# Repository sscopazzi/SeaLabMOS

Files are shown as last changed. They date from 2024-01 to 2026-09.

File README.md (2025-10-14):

This work will be presented at MTS Great Lakes in 2025. If curious, I can send you the paper in prep, or check out [my website's page](https://www.sophiescopazzi.com/projects/sealabmos) for some pictures.

## Current Supported System Types

1. **Traditional CTD**: Salinity, temperature, depth sensors with three variants: 1.5in and 2.0in PVC (~140m) or 2.0in steel pipe (~350m)  
2. **Temperature logger**: Temperature only monitoring for a ~few days to ~two weeks, based on system configuration
3. **Bottom Pressure Recorder**: Pressure only for tide measuring, research ongoing for three used in conjuction for wave height and direction
4. **Surface Float**: All sensors optional. Salinity, water temperature, GNSS/location, LED beacon, atmospheric pressure/temperature, light, etc.



### Base Datalogger Hardware

| **Name** | **Adafruit Part** # | **What it does** | **Accuracy** | **Cost** |
|------|------------------|---------------|----------|------|
| [Adafruit Feather RP2040 Adalogger w/ microSD Card](https://www.adafruit.com/product/5980) | 5980 | Datalogger | — | \$15 |
| [SD/MicroSD Memory Card (512 MB)](https://www.adafruit.com/product/5252) | 5252 | Data storage | — | \$5 |
| [DS3231 Precision RTC FeatherWing](https://www.adafruit.com/product/3028) | 3028 | Real time clock | ±2 minutes per year | \$14 |
| [CR1220 12mm Diameter 3 V Lithium Coin Cell Battery](https://www.adafruit.com/product/380) | 380 | Battery for RTC | — | \$1 |
| [Lithium Ion Battery Pack 3.7 V 2.2 Ah (or 2.5–10 Ah)](https://www.adafruit.com/product/1781) | 1781 (2.2 Ah) | Battery | — | \$10 |
|      |      |      |      |      |
|      |      |      |      |      |
| **Display**     |      |      |      |      |
| [Adafruit FeatherWing 128×64 OLED Display (optional)](https://www.adafruit.com/product/4650) | 4650 | Screen, buttons | — | \$15 |
|      |      |      |      |      |
|      |      |      |      |      |
| **Location**      |      |      |      |      |
| [Mini GPS (PA1010D)](https://www.adafruit.com/product/4415) | 4415 | GPS/GNSS, Time | Testing 10 Hz | \$30 |
| [Ultimate GPS Breakout (PA1616D)](https://www.adafruit.com/product/5440) | 5440 | GPS/GNSS, Time | Testing, 10 Hz | \$30 |
| [External Active GPS Antenna](https://www.adafruit.com/product/960) | 960 | For Ultimate | Testing | \$21.5 |
| [High-strength 'rare earth' magnet](https://www.adafruit.com/product/9) | 9 | Hold antenna | — | \$2.5 |
|      |      |      |      |      |
|      |      |      |      |      |
| **Sensor Cables**      |      |      |      |      |
| [STEMMA QT / Qwiic JST SH 4-pin Cable](https://www.adafruit.com/product/5385) | 5385 | Sensor connection | — | \$1–1.5 |
| [STEMMA QT / Qwiic 5 Port Hub](https://www.adafruit.com/product/5625) | 5625 | Sensor connection | — | \$2.5 |

### Sensors  

| **Type** | Part # | Variable | Depth Rating (m) | Response Time | Accuracy | Cost |
|---|---|---|---|---|---|---|
| [Atlas Scientific Mini Conductivity K 1.0 Kit](https://atlas-scientific.com/kits/mini-conductivity-k-1-0-kit/) | — | Conductivity | 353 | 90% in 1 s | 99% in 1 s | \$200 |
| [Waterproof 1-Wire DS18B20](https://www.adafruit.com/product/381) | 381 | Temperature | Not specified | 60% in 12 s, 90% in 31 s | ±0.5 °C | \$15 |
| [DS18B20 Extender](https://www.adafruit.com/product/5971) | 5971 | DS18B20 accessory board | — | — | — | \$— |
| [10K Precision Epoxy Thermistor](https://www.adafruit.com/product/372) | 372 | Temperature | Not specified | 60% in 3 s, 90% in 7 s | ±0.1 – 0.5 °C | \$4 |
| [Platinum RTD Sensor – PT100](https://www.adafruit.com/product/3290) | 3290 | Temperature | Not specified | — | — | \$— |
| [PT100 RTD Amplifier – MAX31865](https://www.adafruit.com/product/3328) | 3328 | Amplifier for PT100 | — | — | — | \$— |
| [Atlas Scientific K 1.0 Kit](https://atlas-scientific.com/kits/mini-conductivity-k-1-0-kit/) | — | Conductivity | 353 | 90% in 1 s | 90% in 1 s | \$200 |
| [Blue Robotics Celsius Fast-Response (TSYS01)](https://bluerobotics.com/store/sensors-cameras/sensors/celsius-sensor-r1/) | — | Temperature | 975 | 3 s (90% in 2 s, measured) | ±0.1 °C | \$70 |
| [Blue Robotics Bar02 / Bar30 / Bar100 (pressure options)](https://bluerobotics.com/product-category/sensors-cameras/sensors/) | — | Pressure | 10m, 300, 1,000m | — | — | \$80, \$90, \$380 |

> *Note:* Response time and accuracy are from manufacturer specs and initial testing. For reduced costs, static deployments may not need a pressure sensor.  
> Depth rating for temperature sensors not from Blue Robotics are not specified by manufacturers and depends on sealant/epoxy.

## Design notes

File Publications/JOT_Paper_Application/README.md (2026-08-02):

# Figures for "Conductivity Accuracy of Two Open Source SeaLabMOS CTDs"

Open `SeaLabMOS-JOT-app-paper.ipynb` and run all cells in order: the master CONFIG cell, the three loader sections, then any figure cell in any order. Figure cells never depend on each other. All paths are relative to the notebook, so this folder can be moved, zipped or cloned anywhere and still run.

To see photos of what the systems look like, [please see my website](https://www.sophiescopazzi.com/projects/sealabmos).

Figures are written to `plots/` as `figNN_*.png` at 600 dpi, numbered to match the paper. The list of required packages is fairly standard (there is an environment.yml if you need it).
  - python=3.12
  - numpy=2.4.4
  - pandas=3.0.2
  - scipy=1.17.1
  - matplotlib=3.10.8
  - xarray=2026.7.0
  - netcdf4=1.7.4 # conda package name is lowercase; imported as netCDF4
  - gsw=3.6.23 # TEOS-10 / PSS-78, provides gsw.SP_from_C

## Layout

Every data file sits directly in `data/`, prefixed by experiment. The two units MIS_1 and MIS_2 did not do the same things: MIS_1 was used on the workbench in the lab and MIS_2 was used for the stepped casts. Both took part in the bucket tests. In all cases, the ground truth was the RBR system.

```
SeaLabMOS-JOT-app-paper/
├── SeaLabMOS-JOT-app-paper.ipynb
├── README.md
├── environment.yml
├── requirements.txt
├── .gitignore
├── data/
│   ├── lab_MIS_1.csv                          lab standards, MIS_1
│   ├── lab_204386_20260703_1802.nc            lab standards, RBR          (+ .rsk)
│   ├── bucketA_MIS_1.csv                      Jul-3 bucket A, MIS_1
│   ├── bucketB_MIS_1.csv                      Jul-3 bucket B, MIS_1
│   ├── bucketA_MIS_2.csv                      Jul-3 bucket A, MIS_2
│   ├── bucketB_MIS_2.csv                      Jul-3 bucket B, MIS_2
│   ├── bucket_204386_20260703_1829.nc         Jul-3 buckets A and B, RBR  (+ .rsk)
│   ├── cast_MIS_2_2026-07-11T21-12-38.csv     Jul-11 stepped casts, MIS_2
│   ├── cast_204386_20260711_1639.nc           Jul-11 stepped casts, RBR   (+ .rsk)
│   └── static_frame/                          bottom-frame deployment, Jun 5-9
│       ├── long_originalCTD_2026-06-07T06-41-00.csv   co-deployment, originalCTD
│       ├── long_204386_20260609_2023_00008.nc         co-deployment, RBR
│       ├── profiles_originalCTD/              16 originalCTD casts
│       │   └── originalCTD_<stamp>.csv
│       └── profiles_rbr/                      17 RBR cast profiles
│           └── rbr_204386_<log>_<nnnnn>.nc
└── plots/                                     figNN_*.png at 600 dpi, tracked in git
```

## Figures

| Fig | Content |
|----|----|
| 1  | Experiment timeline |
| 2  | Lab setup photograph (not a plot, no cell in the notebook) |
| 3  | Temperature 1:1 vs RBR: pooled casts + static co-location |
| 4  | Implied EC gain, both units + MIS_1 pipeline |
| 5  | Depth vs time, both stepped casts |
| 6  | Firmware-reported salinity profiles |
| 7  | 1:1, firmware vs recalculated salinity at hold averages |
| 8  | EC_GAIN fit + two bucket-test insets |
| 9  | Four salinity pipelines vs RBR, MIS_1 workbench |
| 10 | Out-of-sample bucket validation for MIS_1 and MIS_2 |
| 11 | Salinity profiles: RBR, firmware and recalculated |
| 12 | GOFS 3.1 vertical level distribution |

## Corrections to Salinity Data

To sum up results of the paper in one sentence, MIS_1 and MIS_2 need a system-specific correction, applied to electrical conductivity before the PSS-78 call (never as an additive offset on salinity):

- **MIS_1**: quadratic, `EC_corr = 0.86331·C + 0.0149285·C²`, fit on the six lab
  calibration standards through the origin.
- **MIS_2**: scalar, `EC_corr = EC_GAIN_MIS2 · C`. MIS_2 never ran against the
  lab standards, so its gain comes from the thirteen equilibrated hold points of
  the 2026-07-11 stepped casts. It's `EC_GAIN_MIS2` = 0.9908. 

`C` used in is `gsw.SP_from_C` in mS/cm. The [Atlas Scientific salinity sensor (EZO)](https://atlas-scientific.com/kits/mini-conductivity-k-1-0-kit/) logs µS/cm, so every pipeline divides by 1000 beforehand. There is no single `EC_GAIN`. **Each correction is system-specific.**

`EC_GAIN_MIS2` is **fitted at run time**, not assumed. The hold points it is fit on carry whatever depths `DEPTH_ZERO_MODE` produces, so the gain and the depth
zero stay consistent. 

Firmware-reported salinity (`sal_fw`) is not corrected and **is not a data product**. It appears in Figures 6, 7 and 11 only to show why it is discarded. The EZO hard-codes 25 °C in its temperature compensation and applies no pressure term (that I can find information about).

## Data Notes

Every file is read by at least one figure, except the `.rsk` files, which are the RBR system originals kept for provenance. The notebook reads the `.nc` exports Ruskin produced from them.

| File | Used by |
|----|----|
| `lab_MIS_1.csv` | Figures 4, 9, 10 |
| `lab_204386_20260703_1802.nc` | Figures 4, 9, 10 |
| `bucketA_MIS_1.csv` | Figure 10 |
| `bucketB_MIS_1.csv` | Figure 10 |
| `bucketA_MIS_2.csv` | Figures 4, 8 inset, 10 |
| `bucketB_MIS_2.csv` | Figures 4, 8 inset, 10 |
| `bucket_204386_20260703_1829.nc` | Figures 8, 10 |
| `cast_204386_20260711_1639.nc` | Figures 5–8, 11 |
| `cast_MIS_2_2026-07-11T21-12-38.csv` | Figures 5–8, 11 |

Figures 1 and 12 require no data files. Figure 1 is built from hand-written timestamps in the loader CONFIG, Figure 12 from the transcribed GOFS [vertical level list](https://www.hycom.org/dataserver/gofs-3pt1/analysis).

The bottom of every RBR cast is trimmed by 0.1m where it contacted the muddy bottom, effecting the salinity value by sometimes up to 6.7 PSU (`RBR_BOTTOM_TRIM_M = 0.10`).

Figure 3 reads everything under `data/static_frame/`: the 17 `originalCTD_*.csv` casts, the 17 RBR cast profiles they pair against, and the long log. 16 are casts and 15 of those pair one-to-one with a profile; `originalCTD_2026-06-07T06-05-42.csv` has two casts in the same data file and thus is split into `_a` and `_b`. `long_originalCTD_2026-06-07T06-41-00.csv` is the long co-deployment and the loader selects it as `LONG`.

A keen viewer will see the numbers of the RBR casts are not sequential. Left out of `static_frame/profiles_rbr`: two RBR profiles `20260609_2023` numbers `_00002` and `_00020`, plus `20260606_0625_00001` where they do not have a paired cast.

Also missing are the two casts from the long deployment: `RBR_00007` is the descent into it and `RBR_00009` is the recovery. 

Nothing in the matcher looks at depth, so `MAX_DEPTH_MISMATCH_M = 1.0` in the pairing cell checks afterwards: a paired cast and profile should reach nearly
the same depth, and anything further apart is reported by name. It warns rather than drops, since a wide pair may still be legitimate. On the shipped data every pair passes, the worst being 0.38 m.

**For the stepped cast hold depth matching:** 15 holds are detected, but they become the 13 points in the Figure 8 because the RBR binned profile spans 0.22–9.80 m, and two MIS_2 surface holds sit above the RBRs shallowest bin with nothing to match against. Both are hold segments inside `cast_MIS_2_2026-07-11T21-12-38.csv` and are not separate files (two holds very 
close to the surface done with the MIS_2 and not RBR). These holds outside the binned RBR profile are dropped explicitly instead of silently taking an end-bin value.

## Font sizes

`FS_GLOBAL` in the master CONFIG controls every figure for consistency. 
Each figure cell opens with `fonts()`, which resets the six `FS_*` globals 
before drawing, so a size set inside one cell cannot leak into the next regardless 
of order ran. To change one figure only, pass the override to its own call, e.g. `fonts(FS_TICK=14)`, or just hardcode the line (as done in a few places for figure legibility and formatting).

## The SeaLabMOS Clocks and Time Issues

The absolute time from MIS_1 and MIS_2's clocks for the buckets was incorrect. On power-on the system initialised its clock to the firmware compile time, so the time record starts at the time that firmware was uploaded, regardless of true power-on time. This firmware bug has since been fixed. Elapsed time *within* one record is reliable and used for hold detection, transit rates, the Figure 5 time axis. 

The originalCTD and MIS_2's stepped cast (I found the firmware bug between the buckets and stepped cast) didn't have the time bug, but they carried a daylight-saving hour added to a UTC clock because the firmware was uploaded before DST happened (in the case of the originalCTD) or I put the wrong ZD in the firmware for DST (in the case of MIS_2).

- **Buckets are matched by which water.** Each instrument has its own window in its
  own clock. What ties them together is that both sampled the same bucket. The system's mean over its window is the reference salinity for the system in their respective buckets.
- **Casts are matched by time.** The Jul-11 stepped casts and the originalCTD casts carry a daylight-saving hour on an otherwise sound UTC clock; removing it (`MIS2_CAST_DST_FIX_H`, `APPLY_DST_FIX`) makes their timestamps directly comparable with the RBR, and cast-level pairing in the static-frame section is done on overlapping time interval, with maximum-depth agreement as an independent check.

## Atmospheric pressure and depth

Atmospheric pressure is **not** taken per cast from a barometer. `ATM_MBAR = 1013.25` is a nominal standard atmosphere, and the RBR independently uses its own default_atmospheric_pressure` of 10.1325 dbar, the same nominal value.

That constant enters results by two different routes.

**Through the PSS-78 pressure term.** `p_dbar` is passed to `gsw.SP_from_C`, where pressure barely matters: an error of 0.2 dbar moves salinity by 0.00005 PSU, and 2 dbar by 0.0005 PSU. This is why the bucket and lab work is unaffected regardless of the weather.

**Through the depth matching.** Each hold takes its reference by interpolating the RBR profile in depth, so a depth error maps straight onto a salinity error through the stratification.

### Zeroing the depth against in-air samples

`DEPTH_ZERO_MODE` in the master CONFIG selects what defines 0 m for MIS_2's stepped casts, using the samples where `ec` falls below `AIR_EC_MAX` (probe out of water). It changes Figures 5, 6, 7, 8 and 11; Figures 1, 4, 9, 10 and 12 are untouched.

| Mode | Offset subtracted | Fitted gain | Fit RMSE |
|----|----|----|----|
| `none` — firmware `brDepth` as-is | 0.0000 m | 0.9908 | 0.0629 PSU |
| `pre_cast_air` | 0.1488 m | 0.9898 | 0.0533 PSU |
| `post_cast_air` (default) | 0.0059 m | 0.9908 | 0.0626 PSU |

`post_cast_air` is the default: its in-air window sits after the cast, so it zeros the depth using the closest thermal state of the pressure sensor to the temperature of the water. 
 `none` gives the same 0.9908 the paper prints, because the firmware's own zero happens to land 0.0059 m from the post-cast in-air reading. This is luck rather than a reason to trust the firmware zero.

**The two in-air references disagree, and the reason is temperature, not weather.** The pressure reading moves with sensor temperature (roughly +2.9 mbar/°C within this record):

| In-air window | Sensor T | brPressure | brDepth |
|----|----|----|----|
| before the first cast (dry and hot from being in the sun, just powered on) | 26.1 °C | 1028.06 mbar | +0.1488 m |
| after the last cast (wet, 13 min later) | 21.1 °C | 1013.65 mbar | +0.0059 m |

Atmospheric pressure does not fall 14.5 mbar in 13 minutes. The sensor cooled 5 °C and the reading followed. During the casts the sensor sits at 20.3 °C (close to the post-cast in-air state), roughly 6 °C from the pre-cast one. So `pre_cast_air` derives its zero from both a thermal state the instrument was not in while measuring,  and from temperature warmer than the water, and `post_cast_air` derives it from very nearly the right one.

The loader prints all three offsets and the sensor temperature in each state on every run, and warns when the two in-air references differ by more than 0.05 m.

**Pre vs post-cast pressure is on our list for further study**. This should especially be compared to a weather station [like this one](https://github.com/sscopazzi/Portable_Weather_Station).

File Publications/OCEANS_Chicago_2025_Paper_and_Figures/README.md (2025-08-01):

# SeaLabCTD MTS Paper Deployments and Figures

This folder contains plots, results, and analysis scripts from the series SeaLabCTD tests conducted April to July 2025 conducted immitely offshore the Valdez Marine Termina, in Port Valdez, Prince William Sound, Alaska. Each folder represents a different deployment.

---

### Tools Used
- Python (pandas, matplotlib, numpy, scipy, etc.)
- GSW (Gibbs SeaWater) Oceanographic Toolbox
- Arduino + Feather RP2040 Logger Firmware (see manual)
- Atlas Scientific + Blue Robotics sensors
---

### Notes
- All data is timestamped ISO 8601 format with "-" substituted for ":" for filename restrictions.
- `.csv` files in each directory contain "cleaned" data (only the relevent downcast). Sometimes there are two downcasts.
- The figures below are in the MTS paper.
---

### Contact

For questions, please ask Sophie Scopazzi. Contact information on [my website](https://www.sophiescopazzi.com/)

---

### Figures Overview

All figures used in MTS paper. All figures are located in their respective test folders. Alt text is provided for accessibility.

### Figures Overview

All figures used in the MTS paper. All figures are located in their respective test folders. Alt text is provided for accessibility.

### Figures Overview

All figures used in the MTS paper. All figures are located in their respective test folders. Alt text is provided for accessibility.

| Figure | Description |
|--------|-------------|
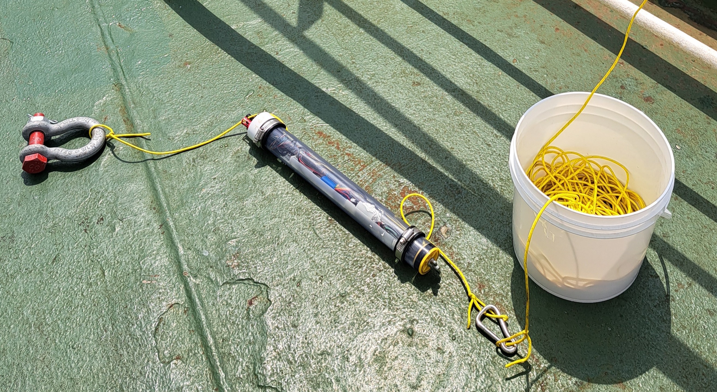
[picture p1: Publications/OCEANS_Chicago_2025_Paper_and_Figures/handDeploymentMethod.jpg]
Hand deployment with SeaLabCTD, shackle and bucket for rope
| **Hand Deployment**<br> | Method used to lower the CTD. A shackle is used as weight; a bucket prevents line tangling. |
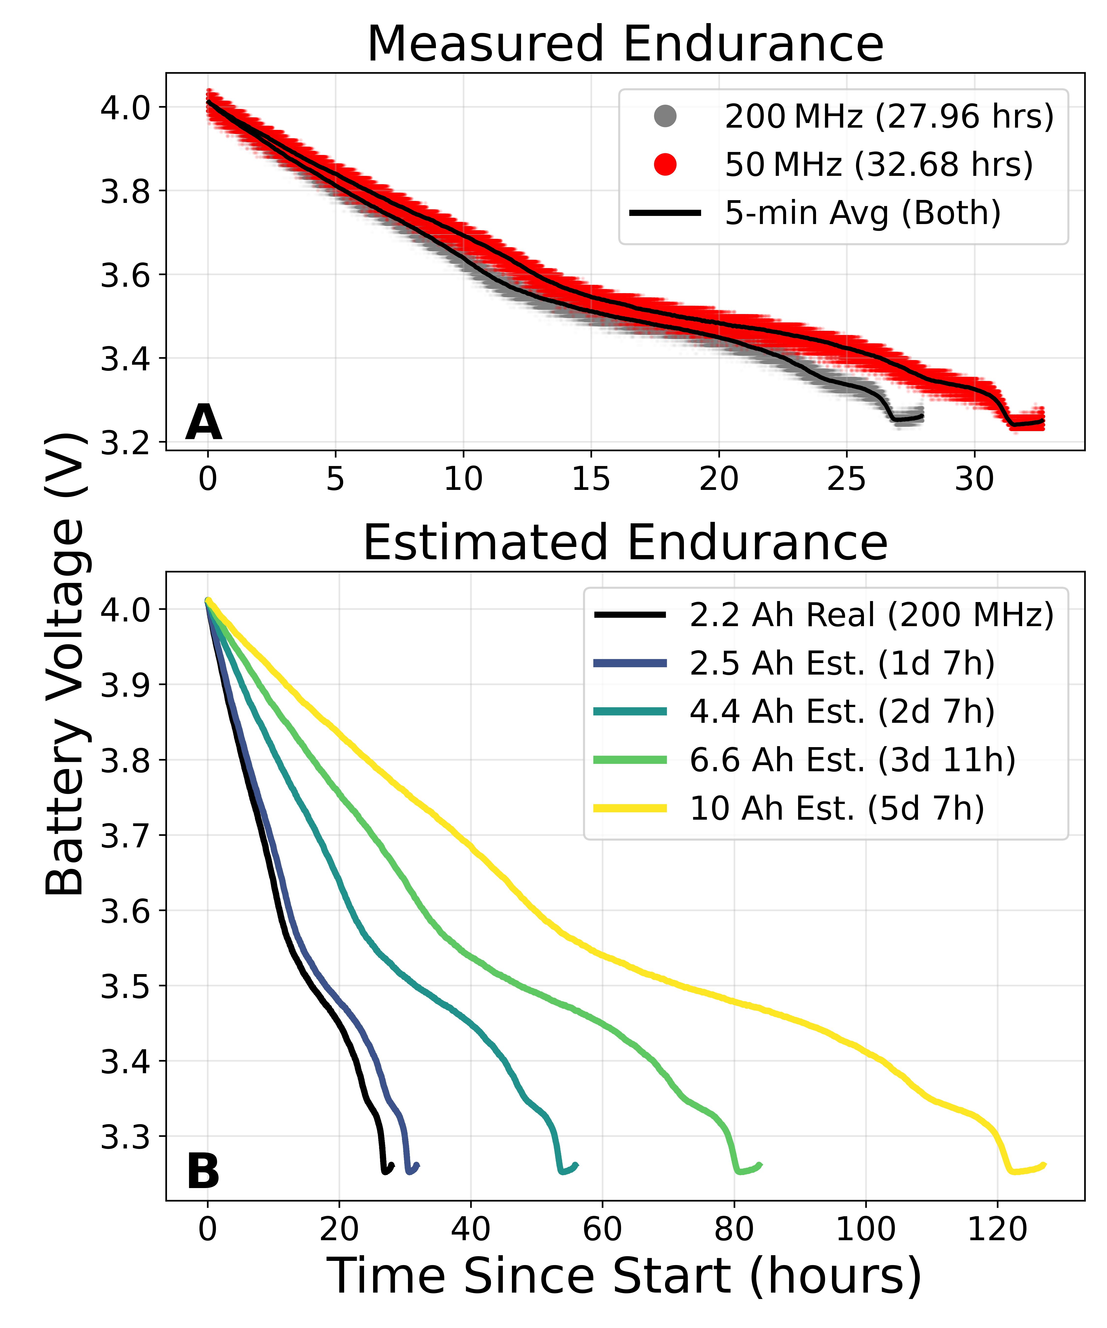
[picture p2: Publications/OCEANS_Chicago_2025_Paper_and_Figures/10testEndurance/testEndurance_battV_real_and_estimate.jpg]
Battery test results showing endurance vs clock speed
| **Battery Endurance**<br> | Runtime comparison at 200 MHz vs 50 MHz. Estimation of endurance for different Adafruit batteries. |
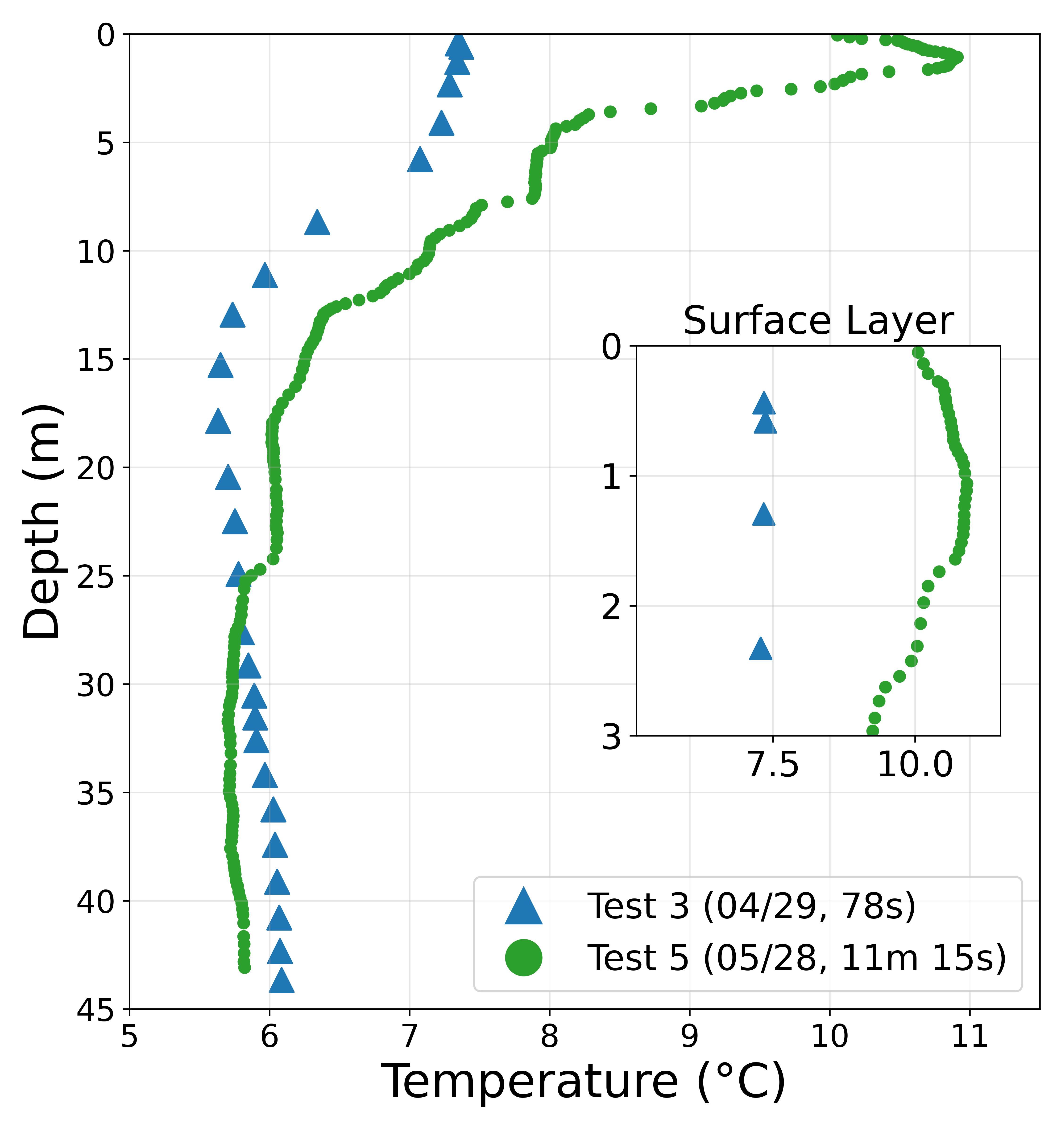
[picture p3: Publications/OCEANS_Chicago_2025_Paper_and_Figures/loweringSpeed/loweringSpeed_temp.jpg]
Deployment speed effect on data resolution
| **Lowering Speed Comparison**<br> | Slow (6.4 cm/s) vs fast (52 cm/s) lowering shows how descent rate affects data fidelity. |
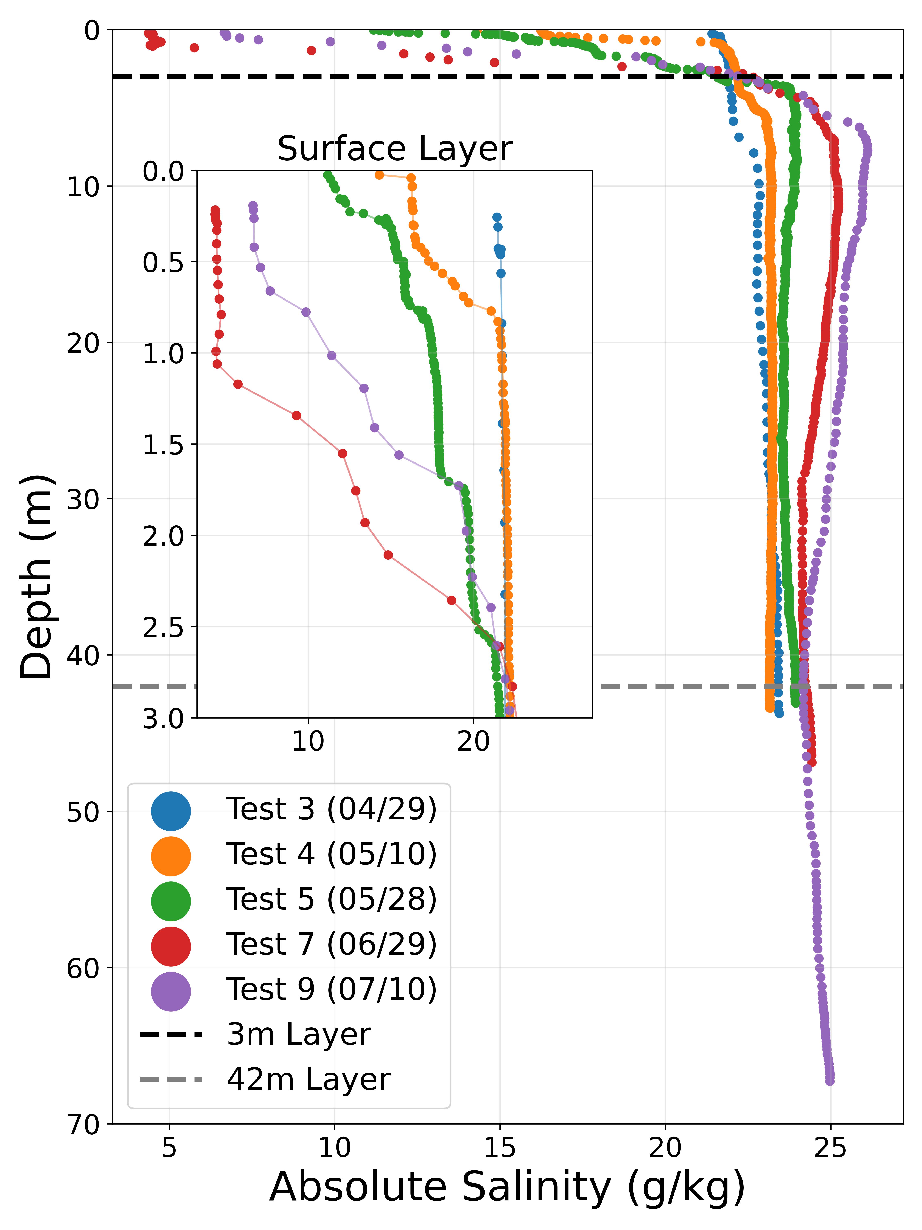
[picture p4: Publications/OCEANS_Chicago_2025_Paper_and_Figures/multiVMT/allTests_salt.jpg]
Salinity profiles from April to July, inset highlights surface layer
| **Salinity Over Time**<br> | Progressive surface freshening and salinity increase at depth across seasons. |
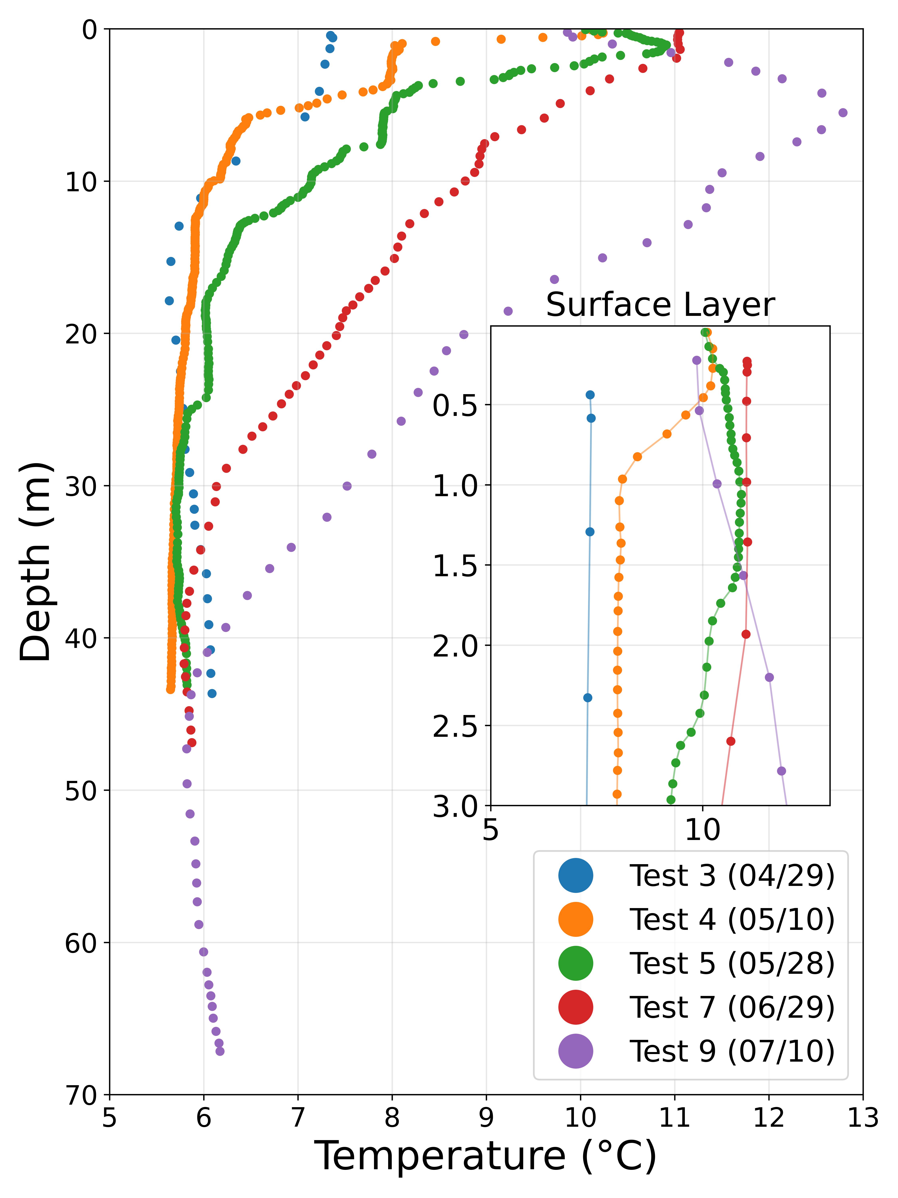
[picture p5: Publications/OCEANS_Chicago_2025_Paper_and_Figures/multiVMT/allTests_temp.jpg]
Temperature profiles from April to July, warmer surface over time
| **Temperature Over Time**<br> | Strong surface warming trend towards summer. Slower casts resolve gradients better. |
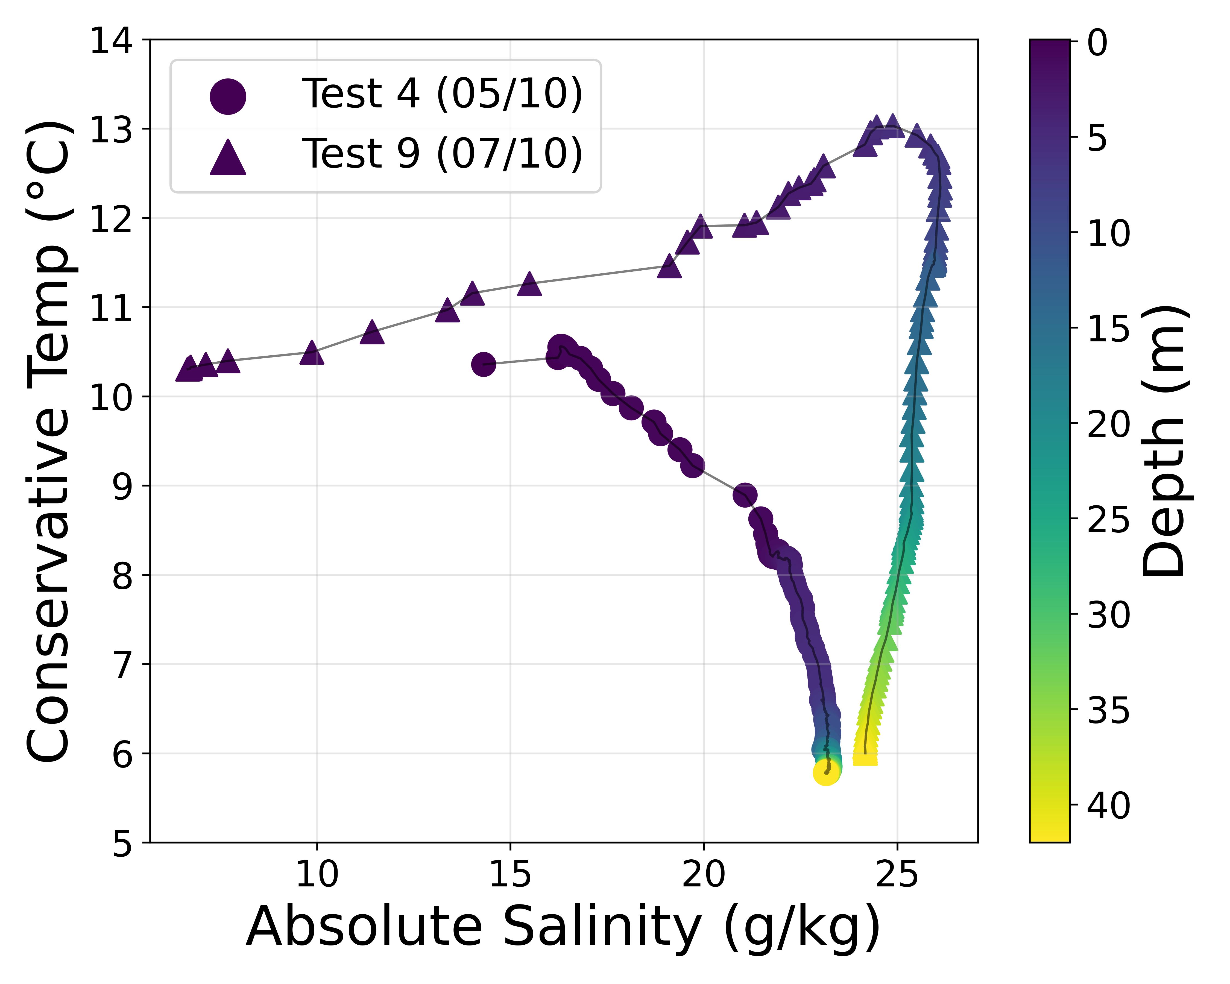
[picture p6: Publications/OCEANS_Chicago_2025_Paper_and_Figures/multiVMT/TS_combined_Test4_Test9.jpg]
T-S plot of two profiles, showing stratification increase
| **Temperature–Salinity (T/S) Diagram**<br> | July water is warmer and saltier. Broader curve shows stronger stratification. |
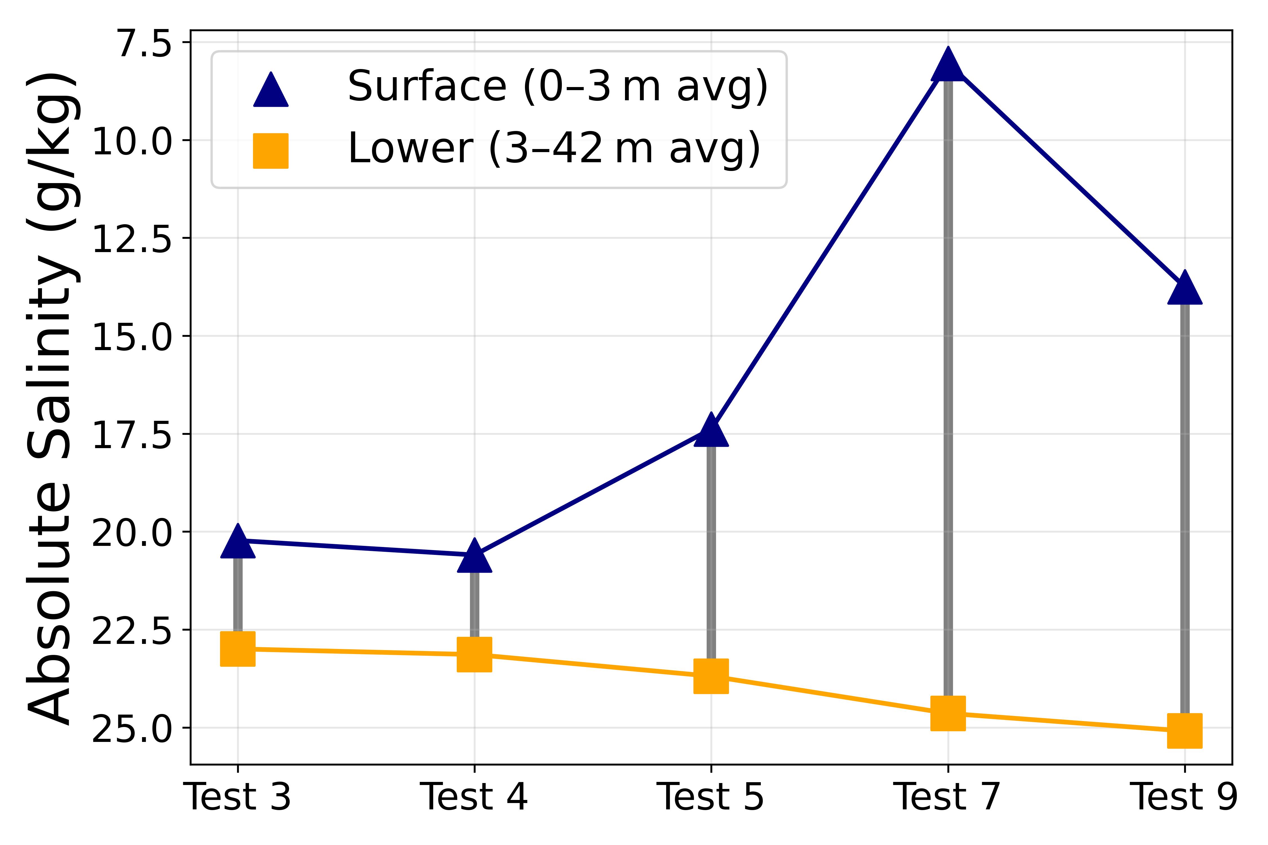
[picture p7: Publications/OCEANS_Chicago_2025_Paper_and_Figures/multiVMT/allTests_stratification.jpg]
Bar chart of surface and deep salinity averages over time
| **Stratification Summary**<br> | Difference between surface and bottom salinity increases over time. |
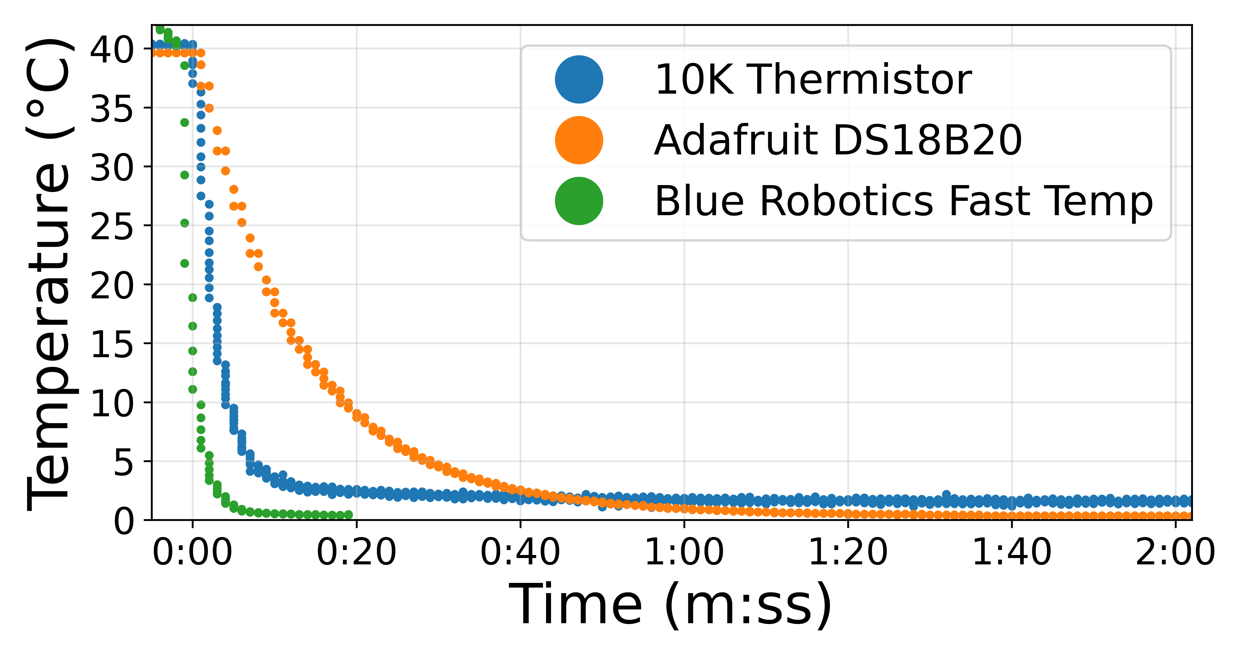
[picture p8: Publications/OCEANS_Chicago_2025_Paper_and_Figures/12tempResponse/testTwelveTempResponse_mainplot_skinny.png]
Thermal response test of three sensors
| **Sensor Response Times**<br> | Response curves from 40 °C then plunge to ice water. Fastest: Blue Robotics Fast Response TSYS01. |
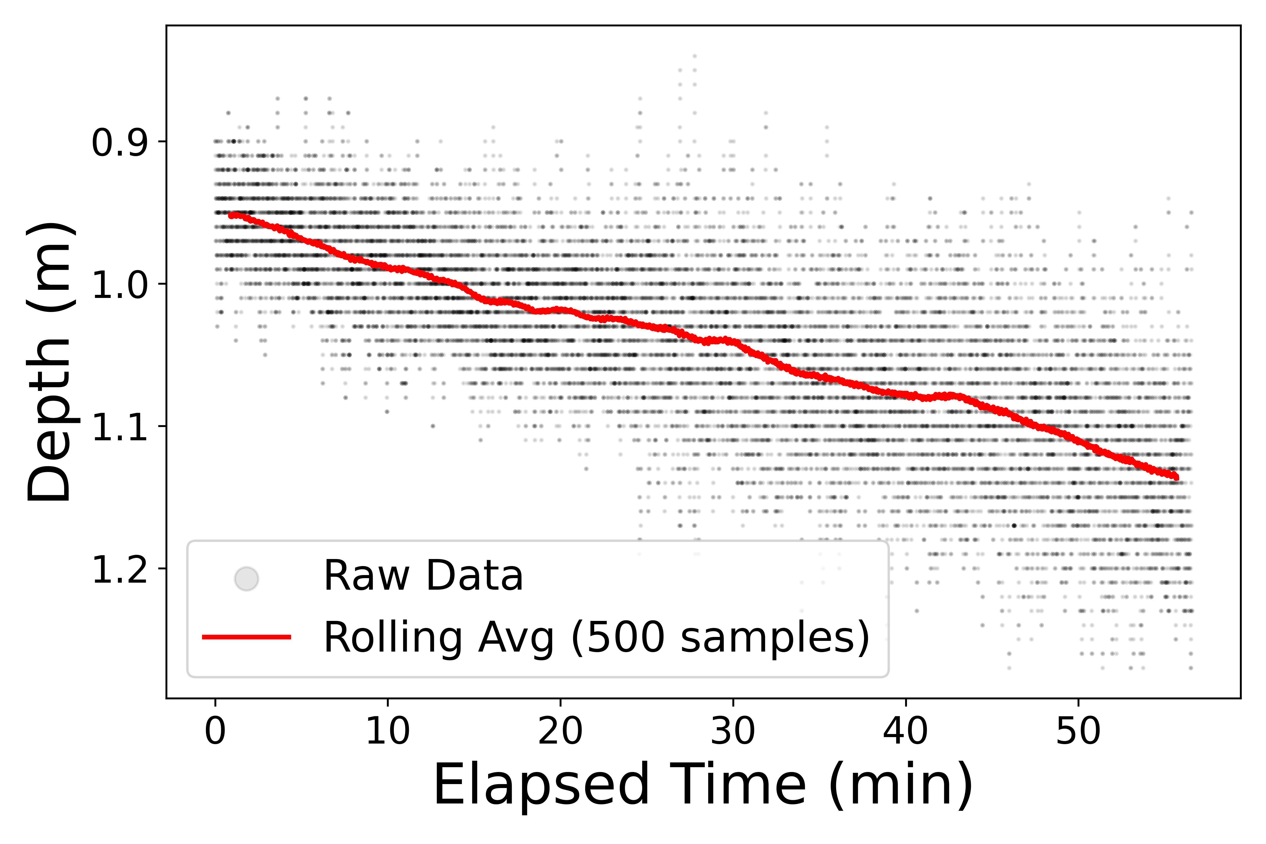
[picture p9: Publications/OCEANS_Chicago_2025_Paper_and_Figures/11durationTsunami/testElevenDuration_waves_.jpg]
Pressure depth trace with long-period trend from tide
| **Tide Rise Time Series**<br> | Static deployment shows incoming tide trend via pressure change. |
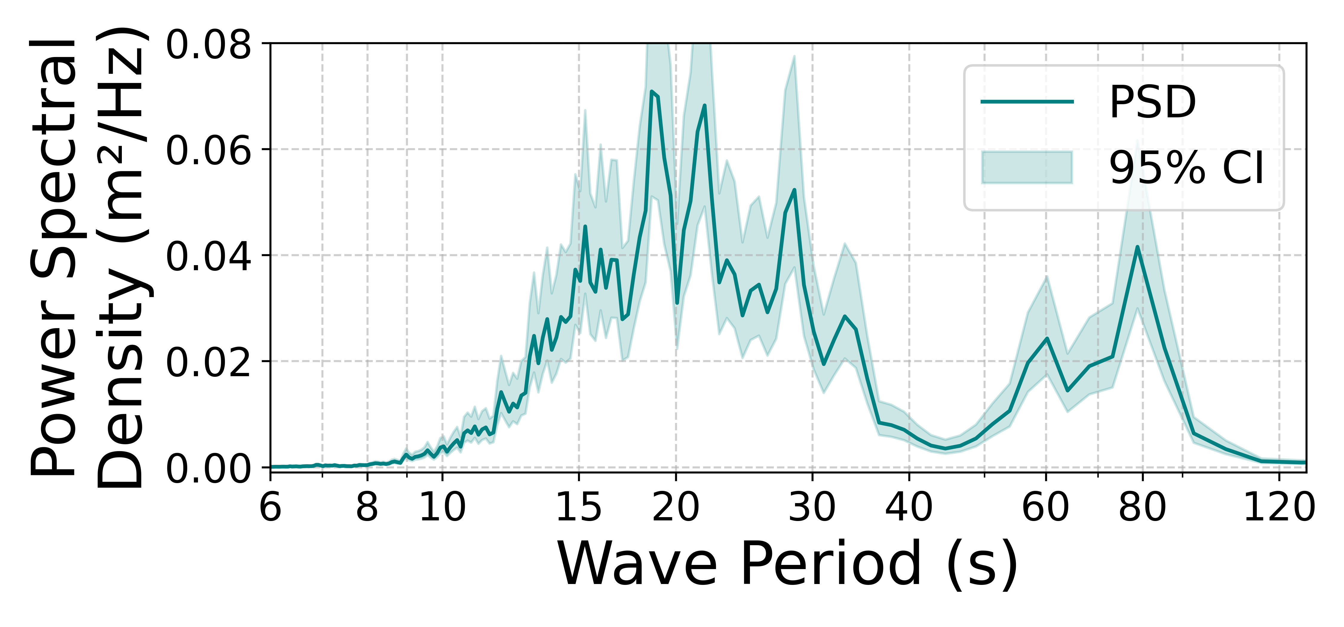
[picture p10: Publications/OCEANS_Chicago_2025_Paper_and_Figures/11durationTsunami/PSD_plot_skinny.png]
PSD analysis of detrended depth data showing wave energy
| **Power Spectral Density (PSD)**<br> | Frequency-domain plot of wave-related motion captured with pressure sensor. |

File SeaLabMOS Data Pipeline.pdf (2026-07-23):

WORK IN PROGRESS | WORK IN PROGRESS | WORK IN PROGRESS
| VERSION 0.1 2026.7.22

Figures were made with assistance of Claude Opus 4.8 High. All writing is my own.

# SeaLabMOS Data Pipeline

### Why disregard the built-in salinity values reported by the Atlas Scientific EZO-EC?

The EZO-EC datasheet stipulates that “when you enable the salinity output of the EZO-EC circuit it mathematically converts conductivity to salinity using the Practical Salinity Scale (PSS-78).” [source]. (https://files.atlas-scientific.com/EC_EZO_Datasheet.pdf) It does this, however, using a default temperature of 25°C. The value it uses can be changed, but resets after the system’s power is reset (on each new power-on). This means that, while it is possible in the firmware to send a mid-deployment in-situ temperature to the EZO-EC and chase accurate values “out of the box” from the EZO-EC, we choose to entirely disregard this data. Even following calibration, the salinity (and if enabled the total dissolved solids and specific gravity) values reported by the EZO-EC are incorrect.
We know this because the EZO-EC does not allow a method of changing the pressure used for its supposed PSS-78 calculation (a formula that requires sea pressure), nor does the documentation state what pressure number is used (if any). The calculation is a “black box” and therefore not to be trusted.
Instead, we opt to do the PSS-78 calculation ourselves from the raw electrical conductivity value as reported by the EZO-EC circuit. This allows full and predictable control over the conversion from EC to salinity using the proper PSS-78 calculation. The additional benefit of using the probe’s raw in-situ EC value is that the probe’s physical interaction with the sea water is by nature taken at the in-situ temperature of the water. Because we accurately know the temperature of the water from the onboard Blue Robotics Fast Temperature sensor [source, source] (https://bluerobotics.com/store/sensors-cameras/sensors/celsius-sensor-r1/) and the pressure from the Blue Robotics Pressure Sensor [source], (https://bluerobotics.com/store/sensors-cameras/sensors/bar-depth-pressure-sensor/) we have all the variables we need: electrical conductivity (in μS/cm which we convert to mS/cm), temperature, and sea pressure.

# SSPP = SP_from_CCCmS/cm, tt C

# ∘ , ppdbar

2026.7.22

## A note on temperature accuracy

Per the datasheet, the absolute accuracy of the temperature sensor is ± 0.1°C between -5 to 50°C[source]. (https://bluerobotics.com/store/sensors-cameras/sensors/celsius-sensor-r1/) Our results have shown it to be more accurate.

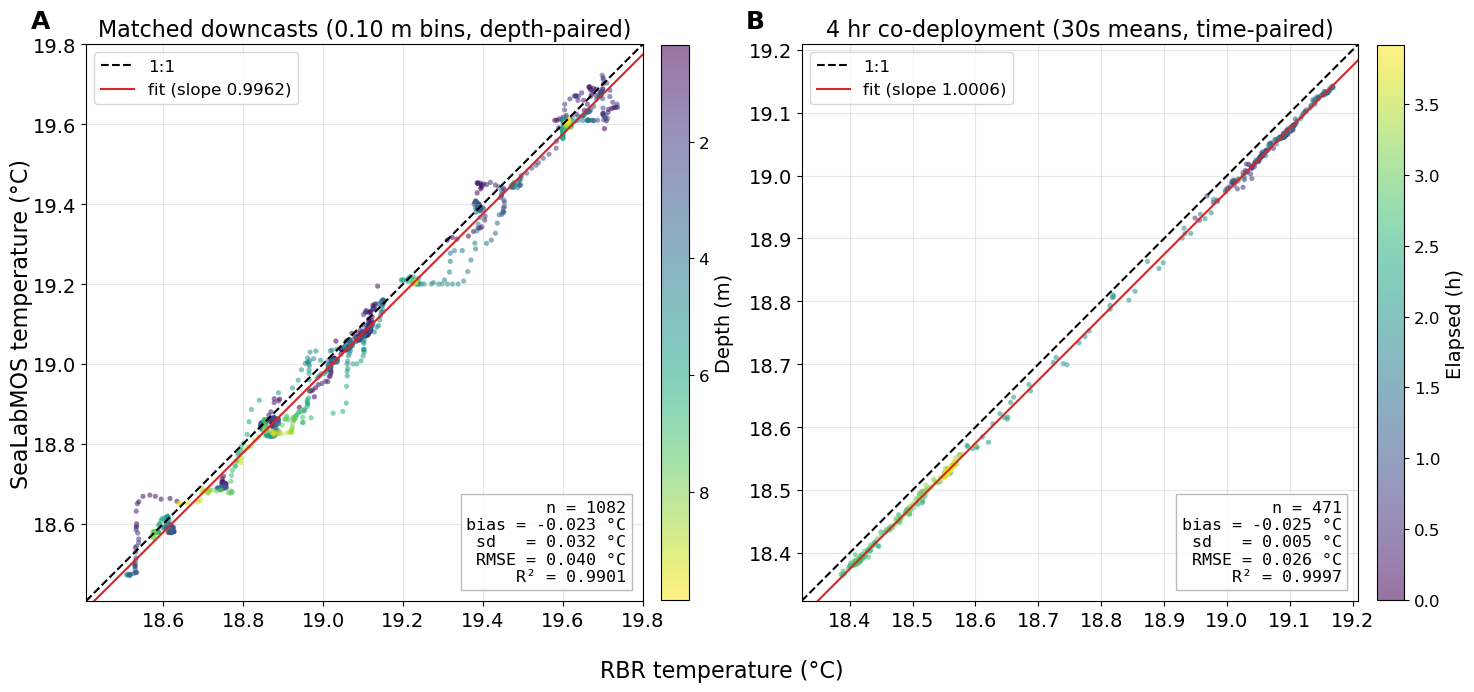
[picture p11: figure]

Panel A pools 17 cast-reference pairs collected over 5 days in the same location. Paired casts were separated by a median of 52 s with a max of 5.4 min. Depth rather than time is used as the pairing axis because the instruments were lowered separately, one after the other, meaning they occupied different depths at any given instant.

Panel B is a 4 hour co-location deployment at the same depth in the same location as A’s casts. The temperature range reflects either the flood current, surface heating/cooling, or any combination thereof. The cause of temperature change is not material to the accuracy assessment.

Panel B gives a mean offset of −0.025 °C with a residual standard deviation of 0.005 °C (n = 471); Panel A gives a mean offset of −0.023 °C with an RMSE of 0.04 °C (n = 1,082). The worst-case 0.04 °C is adopted as the working accuracy figure. Sixteen of seventeen casts show a negative bias, and the two panels agree on its magnitude to within 0.002 °C despite using independent pairing methods. The residual scatter was investigated but not isolated to a single cause.

If we propagate the 0.04 °C into the practical salinity calculation at fixed conductivity it corresponds to 0.005 PSU at 5 PSU, 0.014 at 15, 0.024 at 25, and 0.031 at 33. This is three to twenty times below the platform’s corrected salinity accuracy of ±0.1 PSU. Thus, no temperature correction is applied at any stage; the variable brFastTemp is passed to gsw.SP_from_C uncorrected.

2026.7.22

### Data Pipeline and Variable Names Used

SECTION STILL UNDER CONSTRUCTION
MIS_1 correction in the lab looks quadratic while MIS_2 in the field looked scalar. Given what we know so far, I propose a two pipeline data method before calculating SP_from_C, depending on how the system performs: 1) scalar gain like C_corrected = EC_GAIN × (ec / 1000) and 2) C = ec / 1000, then C_true = A1 × C + A2 × C²
Variable names that I use
sal_fw = raw firmware salinity, trash
sal_recalc = recomputed salinity from raw EC value
sal_recal_sca = final product salinity values after scalar gain correction
sal_recal_qua = final product salinity values after quadratic correction
The default SeaLabMOS CTD’s firmware reports three values from the EZO-EC: electrical conductivity (ec), salinity, and total dissolved solids. Only the first is used.
1. Compute practical salinity using the ec values from the Atlas Scientific EZO-EC circuit and the system’s in-situ temperature via PSS-78 by utilizing GSW-Python SP_from_C[source] (https://teos-10.github.io/GSW-Python/gsw_flat.html)
2. The returned SP value should closely track the RBR, but with the signature of a multiplicative conductivity calibration error intrinsic to the specific SeaLabMOS CTD system (different error per system)
3. Compute a least-squares fit of recomputed vs. reference salinity over the calibration points to find the EC_GAIN correction
4. Apply the EC_GAIN correction factor to the original ec data, then recompute using GSW SP_from_C for final salinity values

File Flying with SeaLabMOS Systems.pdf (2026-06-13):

### Flying with SeaLabMOS Systems (Airport Security Considerations) v2026.06.12

Budget an additional hour to go through security
It is likely that you will end up talking with a member of the TSA’s Bomb Squad. In my experiences at different airports (SFO, HNL, ORD, EWR), they are the most relaxed person to explain things to. Be prepared to talk with the TSA agents at the gate, the Terminal Manager, the police, and maybe even the Airline Representative, all of whom have tended to be less friendly than the Bomb Squad. In my experience, it depends on the airport, the date, and the time.
Arriving and putting your bag through security
1. Do not remove the system from your bag when at the airport and when going through security. It might scare the TSA if you remove it from your bag before the scanner (ask me how I know). Place your bag in the bin / on the conveyor belt and tell the TSA agent standing there that you
a. Have a scientific device consisting of electronics inside a PVC tube that will look weird on the scanner, and
b. That they should call over their supervisor to take a look at it
2. Go through and collect the rest of your belongings, then wait for them to talk to you
At this point, they will start asking you what it is. Nothing bad should happen; calmly explain who you are and what the system is.
Explaining the system
It is an open source oceanographic sampling system (CTD, pressure / temp logger, etc.), considering entirely of consumer-off-the-shelf parts (electronics that anyone can easily purchase online), used to measure things like temperature in the ocean. I recommend trying to split the difference between technical and general language.
When the Bomb Squad person arrives and wants to know about the system itself, explain that it uses
1. Adafruit RP2040 Adalogger MCU and Lithium Ion 3.7V Battery, also from Adafruit
2. Real time clock FeatherWing to record time
3. Sensors - temperature, pressure, salinity, etc. as your system is built
You can pull up my website for images of other systems (also has my contact info): https://www.sophiescopazzi.com/projects/sealabmos
Considerations
1. Don’t make any sudden moves for the bag containing the system or even your own baggage that they screened, and you collected. Follow all of their directions. Stay relaxed and talk to them about what the system is and what it is for
2. You didn’t put the system in your checked bag because you wanted to be on hand to explain what it is – for this exact reason *gesture at everyone gathering*
3. The TSA and/or the police may ask to take a photo of your identification and ticket. They’ve done this every time I’ve flown with the systems and nobody has said anything after
After the Bomb Squad person clears your device for flight, the next issue the Terminal Manager or Airline Representative might bring up is what they have termed “optics”. Even though it’s safe to fly, it can still look scary. As explained to me, “If you stood up on the plane with it in your hands and said something, people would take you seriously.” If optics is brought up, explain that you fully understand and will not be removing it from your baggage until you reach your destination. If this doesn’t satisfy them, offer that they can wrap it in a trash bag a TSA tape (I’ve had to do this once).

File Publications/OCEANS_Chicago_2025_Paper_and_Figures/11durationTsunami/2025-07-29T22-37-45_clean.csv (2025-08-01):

time | deviceMode | vBat | ec | sal | tds | slowDallasTemp | fastBRTemp | slowBRPres | slowBRTemp | slowBRDepth
2025-07-29T22:40:50 | 1 | 3.95 | 50240.00 | 32.92 | 24117.00 | 999.00 | 16.72 | 1104.00 | 16.45 | 0.90
2025-07-29T22:40:51 | 1 | 3.94 | 50240.00 | 32.92 | 24117.00 | 999.00 | 16.71 | 1103.60 | 16.44 | 0.90
2025-07-29T22:40:51 | 1 | 3.95 | 50240.00 | 32.92 | 24117.00 | 999.00 | 16.71 | 1104.10 | 16.44 | 0.90
2025-07-29T22:40:51 | 1 | 3.95 | 50270.00 | 32.94 | 24132.00 | 999.00 | 16.72 | 1105.20 | 16.45 | 0.91
2025-07-29T22:40:51 | 1 | 3.97 | 50270.00 | 32.94 | 24132.00 | 999.00 | 16.71 | 1106.20 | 16.45 | 0.92
2025-07-29T22:40:51 | 1 | 3.94 | 50270.00 | 32.94 | 24132.00 | 999.00 | 16.72 | 1107.00 | 16.45 | 0.93
2025-07-29T22:40:52 | 1 | 3.96 | 50270.00 | 32.94 | 24132.00 | 999.00 | 16.71 | 1107.60 | 16.45 | 0.94
2025-07-29T22:40:52 | 1 | 3.96 | 50270.00 | 32.94 | 24132.00 | 999.00 | 16.72 | 1108.40 | 16.45 | 0.95
2025-07-29T22:40:52 | 1 | 3.97 | 50270.00 | 32.94 | 24130.00 | 999.00 | 16.72 | 1109.80 | 16.45 | 0.96
2025-07-29T22:40:52 | 1 | 3.94 | 50270.00 | 32.94 | 24130.00 | 999.00 | 16.71 | 1110.70 | 16.45 | 0.97
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

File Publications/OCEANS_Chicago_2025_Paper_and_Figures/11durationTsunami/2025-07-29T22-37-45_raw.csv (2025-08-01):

time | deviceMode | vBat | ec | sal | tds | slowDallasTemp | fastBRTemp | slowBRPres | slowBRTemp | slowBRDepth
2025-07-29T22:37:48 | 1 | 3.95 | 999.00 | 999.00 | 999.00 | 999.00 | 15.22 | 1029.50 | 15.88 | 0.16
2025-07-29T22:37:50 | 1 | 3.91 | 999.00 | 999.00 | 999.00 | 999.00 | 15.23 | 1029.40 | 15.90 | 0.16
2025-07-29T22:37:51 | 1 | 3.97 | 0.00 | 0.00 | 0.00 | 999.00 | 15.22 | 1029.70 | 15.90 | 0.17
2025-07-29T22:37:51 | 1 | 3.97 | 0.00 | 0.00 | 0.00 | 999.00 | 15.22 | 1029.90 | 15.91 | 0.17
2025-07-29T22:37:51 | 1 | 3.96 | 0.00 | 0.00 | 0.00 | 999.00 | 15.22 | 1029.10 | 15.91 | 0.16
2025-07-29T22:37:51 | 1 | 3.98 | 0.00 | 0.00 | 0.00 | 999.00 | 15.22 | 1029.90 | 15.91 | 0.17
2025-07-29T22:37:52 | 1 | 3.97 | 0.00 | 0.00 | 0.00 | 999.00 | 15.21 | 1029.60 | 15.91 | 0.16
2025-07-29T22:37:52 | 1 | 3.97 | 0.00 | 0.00 | 0.00 | 999.00 | 15.21 | 1029.90 | 15.91 | 0.17
2025-07-29T22:37:52 | 1 | 3.97 | 0.00 | 0.00 | 0.00 | 999.00 | 15.22 | 1030.00 | 15.91 | 0.17
2025-07-29T22:37:52 | 1 | 3.95 | 0.00 | 0.00 | 0.00 | 999.00 | 15.20 | 1029.50 | 15.91 | 0.16
2025-07-29T22:37:52 | 1 | 3.97 | 0.00 | 0.00 | 0.00 | 999.00 | 15.22 | 1029.50 | 15.91 | 0.16
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

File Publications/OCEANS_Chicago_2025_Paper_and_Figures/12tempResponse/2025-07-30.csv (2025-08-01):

time | deviceMode | vBat | ec | sal | tds | slowDallasTemp | thermTemp | fastBRTemp | slowBRPres | slowBRTemp | slowBRDepth
2025-07-30T13:41:12 | 0 | 3.88 | 999.00 | 999.00 | 999.00 | 85.00 | 23.68 | 999.00 | 999.00 | 999.00 | 999.00
2025-07-30T13:41:12 | 0 | 3.93 | 999.00 | 999.00 | 999.00 | 85.00 | 23.69 | 999.00 | 999.00 | 999.00 | 999.00
2025-07-30T13:41:12 | 0 | 3.82 | 999.00 | 999.00 | 999.00 | 85.00 | 23.73 | 999.00 | 999.00 | 999.00 | 999.00
2025-07-30T13:41:12 | 0 | 3.86 | 999.00 | 999.00 | 999.00 | 85.00 | 23.68 | 999.00 | 999.00 | 999.00 | 999.00
2025-07-30T13:41:13 | 0 | 3.91 | 999.00 | 999.00 | 999.00 | 85.00 | 23.67 | 999.00 | 999.00 | 999.00 | 999.00
2025-07-30T13:41:13 | 0 | 3.80 | 999.00 | 999.00 | 999.00 | 85.00 | 23.74 | 999.00 | 999.00 | 999.00 | 999.00
2025-07-30T13:41:13 | 0 | 3.84 | 999.00 | 999.00 | 999.00 | 22.94 | 23.68 | 999.00 | 999.00 | 999.00 | 999.00
2025-07-30T13:41:13 | 0 | 3.89 | 999.00 | 999.00 | 999.00 | 22.94 | 23.77 | 999.00 | 999.00 | 999.00 | 999.00
2025-07-30T13:41:13 | 0 | 3.87 | 999.00 | 999.00 | 999.00 | 22.94 | 23.67 | 999.00 | 999.00 | 999.00 | 999.00
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

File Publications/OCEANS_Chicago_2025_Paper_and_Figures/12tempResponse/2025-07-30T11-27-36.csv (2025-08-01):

time | deviceMode | vBat | ec | sal | tds | slowDallasTemp | fastBRTemp | slowBRPres | slowBRTemp | slowBRDepth
2025-07-30T11:27:40 | 1 | 3.88 | 999.00 | 999.00 | 999.00 | 999.00 | 21.68 | 1028.70 | 21.29 | 0.16
2025-07-30T11:27:42 | 1 | 3.88 | 999.00 | 999.00 | 999.00 | 999.00 | 21.69 | 1028.50 | 21.32 | 0.15
2025-07-30T11:27:42 | 1 | 3.91 | 0.00 | 0.00 | 0.00 | 999.00 | 21.68 | 1028.50 | 21.33 | 0.15
2025-07-30T11:27:43 | 1 | 3.91 | 0.00 | 0.00 | 0.00 | 999.00 | 21.69 | 1028.60 | 21.33 | 0.15
2025-07-30T11:27:43 | 1 | 3.90 | 0.00 | 0.00 | 0.00 | 999.00 | 21.69 | 1028.60 | 21.33 | 0.15
2025-07-30T11:27:43 | 1 | 3.93 | 0.00 | 0.00 | 0.00 | 999.00 | 21.69 | 1028.20 | 21.34 | 0.15
2025-07-30T11:27:43 | 1 | 3.91 | 0.00 | 0.00 | 0.00 | 999.00 | 21.70 | 1028.50 | 21.34 | 0.15
2025-07-30T11:27:43 | 1 | 3.93 | 0.00 | 0.00 | 0.00 | 999.00 | 21.69 | 1028.30 | 21.34 | 0.15
2025-07-30T11:27:44 | 1 | 3.92 | 0.00 | 0.00 | 0.00 | 999.00 | 21.69 | 1028.30 | 21.34 | 0.15
2025-07-30T11:27:44 | 1 | 3.91 | 0.00 | 0.00 | 0.00 | 999.00 | 21.70 | 1028.20 | 21.34 | 0.15
2025-07-30T11:27:44 | 1 | 3.92 | 0.00 | 0.00 | 0.00 | 999.00 | 21.69 | 1028.80 | 21.34 | 0.16
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

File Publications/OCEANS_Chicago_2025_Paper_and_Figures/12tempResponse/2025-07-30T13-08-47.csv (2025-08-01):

time | deviceMode | vBat | ec | sal | tds | slowDallasTemp | fastBRTemp | slowBRPres | slowBRTemp | slowBRDepth
2025-07-30T13:08:50 | 1 | 3.87 | 999.00 | 999.00 | 999.00 | 999.00 | 20.72 | 1029.80 | 20.99 | 0.17
2025-07-30T13:08:52 | 1 | 3.86 | 999.00 | 999.00 | 999.00 | 999.00 | 20.74 | 1030.20 | 21.03 | 0.17
2025-07-30T13:08:53 | 1 | 3.85 | 0.00 | 0.00 | 0.00 | 999.00 | 20.75 | 1030.10 | 21.03 | 0.17
2025-07-30T13:08:53 | 1 | 3.90 | 0.00 | 0.00 | 0.00 | 999.00 | 20.79 | 1030.10 | 21.04 | 0.17
2025-07-30T13:08:53 | 1 | 3.92 | 0.00 | 0.00 | 0.00 | 999.00 | 20.81 | 1029.70 | 21.05 | 0.17
2025-07-30T13:08:53 | 1 | 3.92 | 0.00 | 0.00 | 0.00 | 999.00 | 20.82 | 1030.00 | 21.05 | 0.17
2025-07-30T13:08:53 | 1 | 3.93 | 0.00 | 0.00 | 0.00 | 999.00 | 20.86 | 1029.60 | 21.06 | 0.16
2025-07-30T13:08:54 | 1 | 3.92 | 0.00 | 0.00 | 0.00 | 999.00 | 20.86 | 1029.70 | 21.06 | 0.17
2025-07-30T13:08:54 | 1 | 3.89 | 0.00 | 0.00 | 0.00 | 999.00 | 20.89 | 1029.60 | 21.06 | 0.16
2025-07-30T13:08:54 | 1 | 3.89 | 0.00 | 0.00 | 0.00 | 999.00 | 20.89 | 1030.00 | 21.06 | 0.17
2025-07-30T13:08:54 | 1 | 3.92 | 0.00 | 0.00 | 0.00 | 999.00 | 20.90 | 1030.10 | 21.06 | 0.17
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

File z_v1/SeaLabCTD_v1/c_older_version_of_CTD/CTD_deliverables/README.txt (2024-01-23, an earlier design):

            ██████╗████████╗██████╗     ██████╗  ██████╗ ██████╗  ██████╗ 
            ██╔════╝╚══██╔══╝██╔══██╗    ╚════██╗██╔═████╗╚════██╗██╔═████╗
            ██║        ██║   ██║  ██║     █████╔╝██║██╔██║ █████╔╝██║██╔██║
            ██║        ██║   ██║  ██║    ██╔═══╝ ████╔╝██║██╔═══╝ ████╔╝██║
            ╚██████╗   ██║   ██████╔╝    ███████╗╚██████╔╝███████╗╚██████╔╝
            ╚═════╝   ╚═╝   ╚═════╝     ╚══════╝ ╚═════╝ ╚══════╝ ╚═════╝ 
                                    readme by Vizi
╔══════════════════════════════════════════════════════════════════════════════════════╗
║ ~ programs ~                                                                         ║
║ ( only use one at a time )                                                           ║
║                                                                                      ║
║   + deployment_programs                                                              ║
║   [ view example log for preview of the data output ]                                ║
║                                                                                      ║
║       * sensorOutput_MULTI_CTD.ino                                                   ║
║           when powered, it will generate a new log file                              ║
║           for each time it's powered on.                                             ║
║           Allowing for easy access of seperate power-ons/deployments                 ║
║                                                                                      ║
║       * sensorOutput_SINGLE_CTD.ino                                                  ║
║           when powered, the data will be put on the end of the                       ║
║           same log file as previous deployments.                                     ║
║           This may be beneificial for some reason.                                   ║
║                                                                                      ║
║   + sensor_testing                                                                   ║
║   [ allows easy testing of sensors ]                                                 ║
║                                                                                      ║
║       * tempSensor_test.ino                                                          ║
║           test temperature sensor                                                    ║
║                                                                                      ║
║       * salinSensor_test.ino                                                         ║
║           test salinity sensor                                                       ║
║                                                                                      ║
║       * pressSensor_test.ino                                                         ║
║           test pressure sensor                                                       ║
║                                                                                      ║
║       * SD_test.ino                                                                  ║
║           validate SD card connection                                                ║
║                                                                                      ║
╠══════════════════════════════════════════════════════════════════════════════════════╣
║ ~ documentation ~                                                                    ║
║                                                                                      ║
║   * README                                                                           ║
║       This file. Surprising isn't it?                                                ║
║                                                                                      ║
║   + datasheets_wiring                                                     		   ║
║       + pressSensor                                                                  ║
║           datasheet and wires                                                        ║
║                                                                                      ║
║       + salinSensor                                                                  ║
║           datasheet and wires                                                        ║
║                                                                                      ║
║       + sdCard                                                                       ║
║           datasheet and wires                                                        ║
║                                                                                      ║
║       + tempSensor                                                                   ║
║           datasheets and wires                                                       ║
║           + temp_calibration_data                                                    ║
║               contains a lot of useful data/info to assist with your temp sensor     ║
║                                                                                      ║
║       * Arduino_Uno_Hole_Diagram                                                     ║
║           used to make the 3D printed file                                           ║
║                                                                                      ║
║       * Housing                                                                      ║
║           end_cap                                                                    ║
║               STL file for end cap                                                   ║
║                                                                                      ║
║           tray                                                                       ║
║               STL file for slideable tray                                            ║
║                                                                                      ║
╠══════════════════════════════════════════════════════════════════════════════════════╣
║ ~ contact ~                                                                          ║
║                                                                                      ║
║   Questions or concerns, contact/ask ACL or Scopazzi                                 ║
║                                                                                      ║
╠══════════════════════════════════════════════════════════════════════════════════════╣
║    special thanks to Vizi (Jasper Scozzafava) for helping with data logging to SD    ║
╚══════════════════════════════════════════════════════════════════════════════════════╝

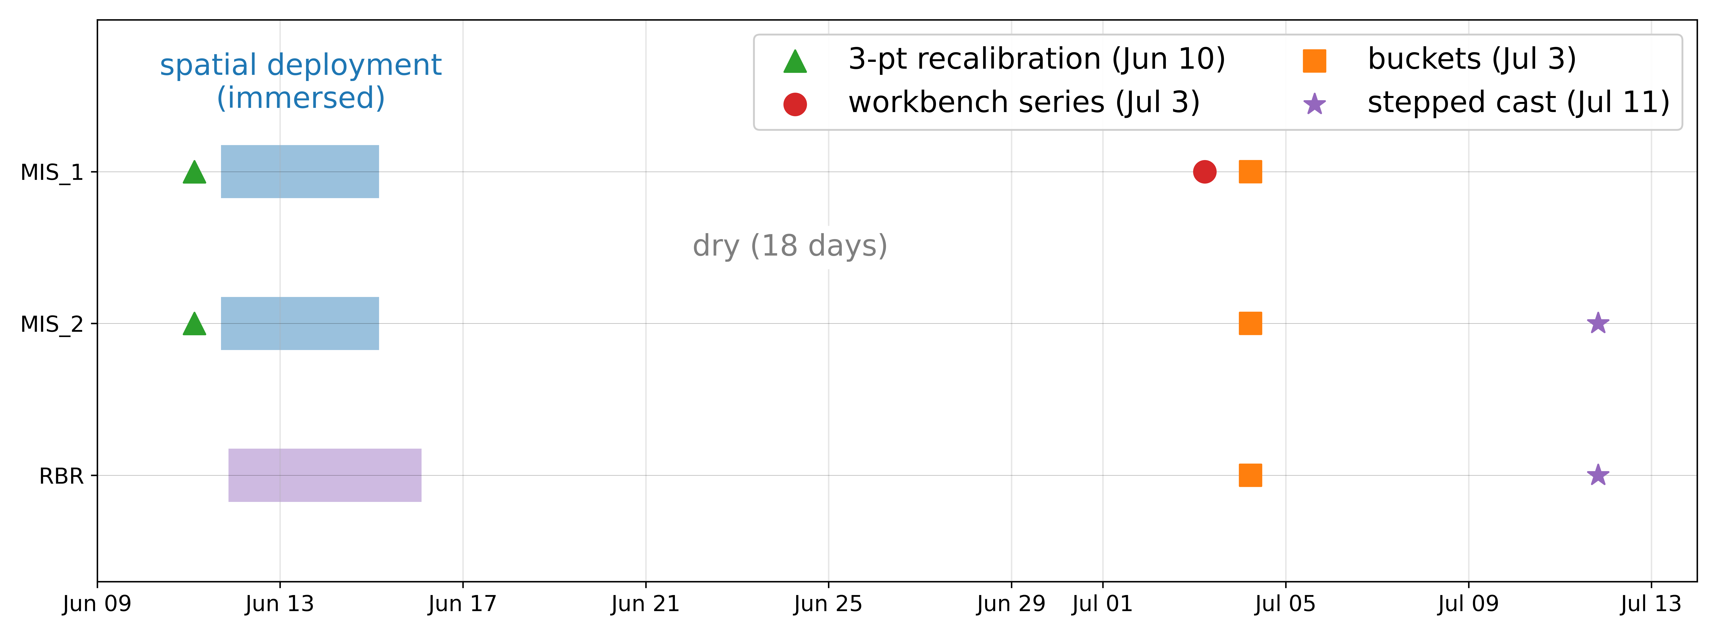
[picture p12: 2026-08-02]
Publications/JOT_Paper_Application/plots/fig01_timeline.png

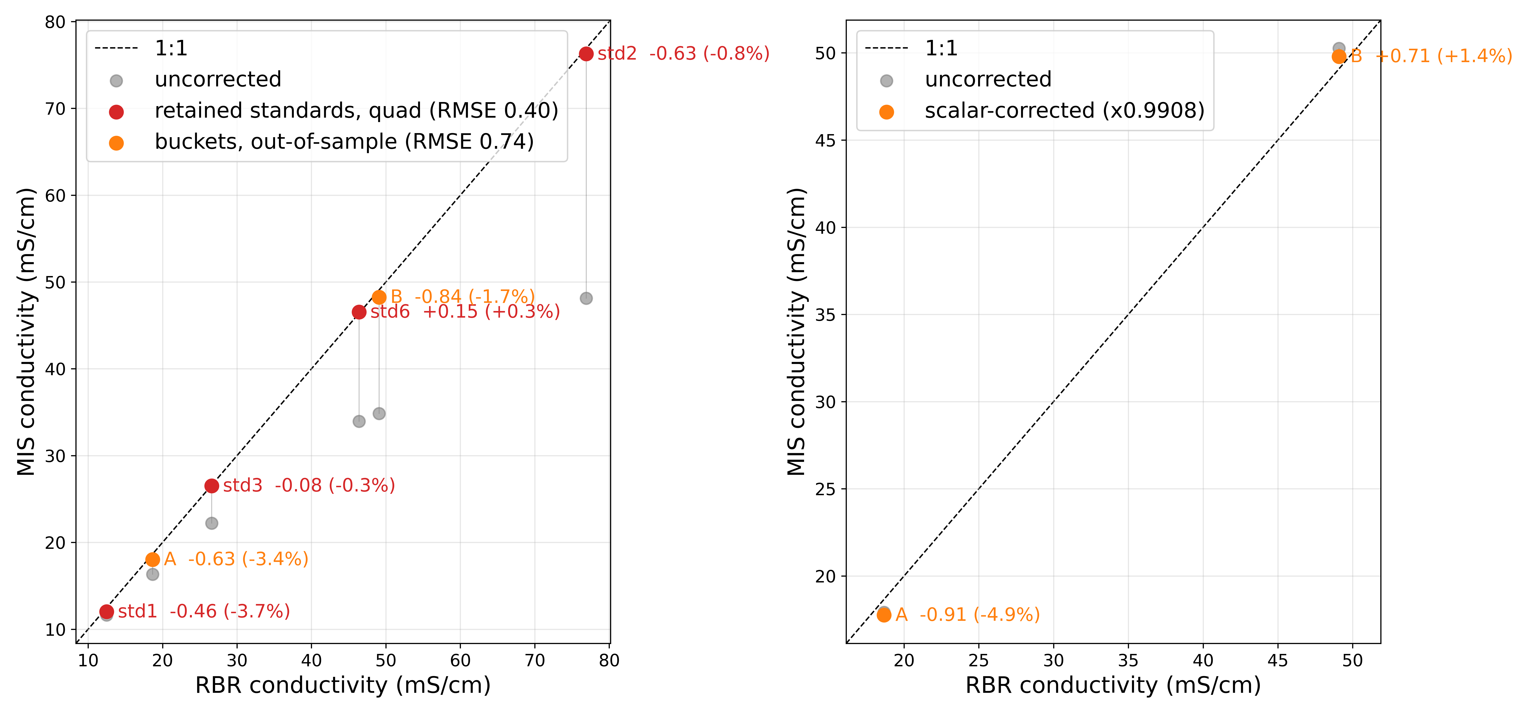
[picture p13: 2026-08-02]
Publications/JOT_Paper_Application/plots/fig10_buckets_out_of_sample.png

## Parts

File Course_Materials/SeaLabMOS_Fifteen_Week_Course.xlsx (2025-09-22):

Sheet: Main
Week | Date | Lecture | Lab | Assignments | Quizzes / Exams | Lecture Topics (expanded) | Lab Topics (expanded)
1 |  | History of ocean observing. Platform and sensor technology used. What is a CTD and what applications does one have? | What is an embedded system? Present CTD building project. Explain and assign hardware. Review sensor data sheets, show resources | Name 5 platforms used for ocean observing and what sensors they may have | What do you hope to gain out of this class and learn by the end of the semester? | 1800s till today. War driven development. Ocean observing systems (the OOS) and platforms they use. NDBC buoys, gliders, UNOLS, wave riders, surface vehicles, and the sensors they use (not talking about satellites). | Show resource I've made, which also points to Adafruit and other online resources. Datasheets for each sensor made by the manufacturer. Sensor limits, etc. Many resources have example code, focusing first on the temperature sensor as it uses I2C (solderless).
2 |  | How to read a sensor data sheet and wire diagram. Types of communication protocols. | Install Arduino IDE. Basic electronic and soldering safety. Soldering workshop. | What is UART / I2C / RS232 / RS484? Benefits and trade-offs of each (matrix?). What is an integer, float, etc., and when to use | What is a CTD and what are they used for? | Review wire diagram reading for CTD, and component parts. What sensors use what type of procol. Pro/con of communicaiton types. Baud rates. UART / I2C, etc. | Electronic safety (power, ground, static, checks before powering anything, multimeter use for continuity and voltage). Soldering workshop - practice soldering headers, resistors, etc. Get battery light kits from ARL at UH for students to take something home (a tangible reward for their work).
3 |  | Using Arduino IDE and C++ to program. Libraries, classes, searching for example code | Integrate temperature sensor with microcontroller. | Temperature sensor | None | Different coding environments / applications. Given a sensor and a microcontroller, how do you connect them? Work through this question in lecture | Connect BlueRobotics' temperature sensor via I2C (solderless). See data in Arduino IDE Serial Monitor
4 |  | Types and pro/con of datafile types (.csv, .netcdf, etc.). Applications of each | Saving sensor data to the SD card. | Everything you need to know to integrate the salinity sensor (data sheet, communication protocol, and example code) |  |  | Add the SD card to the microcontroller and save the temperature data to it.
5 |  | Additive manufacturing, OnShape (not required knowledge for course). Review exam | Integrate salinity sensor | Salinity sensor. | Quiz on sensors so far | Explain different additive manufacturing techniques. Show OnShape as a CAD tool, but it is not required for this class. Exposure to the topic is what is all that is needed. | Hardware and software for salinity sensor. Show data in Serial Monitor
6 |  | Ocean pressure, density. Housing design considerations | Integrate pressure sensor | Pressure sensor. | None |  | Hardware and software for pressure sensor. Show data in Serial Monitor | Install Python and get environment setup and ready to plot. Run example .ipynb in VS Code
7 |  | Anaconda and Python library installation and workshop | Bench test outside housing. Data plotting from test | Data plotting from test, if did not finish in lab | Bench test quiz |  | Bench test the CTD platform. Plot data in Python
8 |  | Exam week | Assemble housing | Ensure Python works. Data plotting from test | Exam 1. All sensors | Plot data from bench testing CTD. | Bench test the CTD platform. Plot data in Python
9 |  | Creating a wire diagram (by hand, KiCad). Class and exam prep. | Housing fitment, ballast tank waterproof test | Show your parents what you make in lab and explain how it works (in person, via video, etc.). How did they react and what were their thoughts? |  | Review what have built so far. How it works and building your own wire diagram (on paper, overview like CAD, expose them to KiCad but not required for this class) | Build housing,add sensors and hardware, test watertight integrity
10 |  | Sensor deployment considerations | CTD testing, troubleshooting | Ensure CTD works | None | How to deploy sensors. Different ways they are deployed based on the science question. Prep idea for vertical transect deployment | Ballasting sensor in salt water. Testing in salt water. Plotting data from test using same plotting code from bench testing
11 |  | Ensure CTD ready for deployment, prep | CTD testing, troubleshooting | Ensure CTD is ready for deployment | None | Functional checkout procedures | Myself as vessel PIC to deploy sensors (or work with Nav Piloting / Small Craft). Tide dependent (outgoing/incoming for salt/fresh)
12 |  | Ensure CTD ready for deployment, prep | Sensor deployment | Ensure CTD is ready for deployment | None | Workshop time. Prep CTD, write code, etc. | Myself as vessel PIC to deploy sensors (or work with Nav Piloting / Small Craft). Tide dependent (outgoing/incoming for salt/fresh)
13 |  | Coding workshop | Plot data from test | Report writing, data plotting | Post-deployment reflection
14 |  | Coding workshop | Plot data from test | Report writing, data plotting
15 |  |  |  | Test week, no assignment | Final Report due
 |  | Attendance (14-15 weeks) | 7 | 0.5 / week (0.1/0.15 per lecture, 0.2 for lab)
 |  | Assignments (5) | 15 | 3pts each
 |  | Quizzes (4) | 20 | 5pts each
 |  | Midterms (2) | 15
 |  | Final report | 28 | +1 extra possible
 |  | Final exam | 15 | Return hardware, review final reports
 |  |  | 100
 |  | Build the CTD so it will float sensor down, and with a place to attach a weight to so it can sit off the bottom
 |  | with a buoy for benthic sampling for extended periods of time. Could leave it during a whole tidal cycle at the bottom.
 |  | Put multuple on the same string to sample the water column
 |  | the saltwater tongue as it comes into the estuary
 |  | do this with and do a few CTD casts next to it while they are all in the water

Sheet: By Day
Week | Day | Lecture | Lab Day | Lab Content | Assignment / Quiz / Exam
1 | 1 | History of ocean observing. Platform and sensor technology | n/a | n/a | Quiz 1. Assignment 1
1 | 2 | History of ocean observing part 2. What is a CTD and what applications does one have? | 1 | What is an embedded system? Present CTD building project. Explain and assign hardware. Review sensor data sheets, show resources | None.
2 | 3 | How to read a sensor data sheet and wire diagrams. Types of communication protocols. | n/a | n/a | Assignment 2
2 | 4 | Soldering theory. Quiz 2. | 2 | Install Arduino IDE. Basic electronic and soldering safety. Soldering workshop. | Quiz 2.
3 | 5 | Using Arduino IDE and C++ to program. Libraries, classes, searching for example code | n/a | n/a | None.
3 | 6 | Anaconda and Python library installation | 3 | Connect to microcontroller. Blink the onboard LED. | None.
4 | 7 | Types and pro/con of datafile types (.csv, .netcdf, etc.). Applications of each | n/a | n/a | Assignment 3.
4 | 8 | Temperature sensor theory | 4 | Temperature sensor integration
5 | 9 | SD card, saving data, theory | n/a | n/a
5 | 10 |  | 5 | Saving sensor data to the SD card
6 | 11 | Salinity sensor theory | n/a | n/a
6 | 12 | Quiz 3. | 6 | Salinity sensor integration
7 | 13 | Ocean pressure, density. Housing design considerations | n/a | n/a
7 | 14 |  | 7 | Pressure sensor integration
8 | 15 | Creating a wire diagram (by hand, KiCad). | n/a | n/a
8 | 16 | Prepare for bench test of CTD. Ensure Python code is ready | 8 | Bench test CTD (outside housing) with all sensors
9 | 17 |  | n/a | n/a
9 | 18 | Exam 1: All sensors | 9 | Data plotting from bench test
10 | 19 |  | n/a | n/a
10 | 20 |  | 10 | Assemble into housing. Fitment. Ballasting.
11 | 21 |  | n/a | n/a
11 | 22 |  | 11 | CTD troubleshooting
12 | 23 |  | n/a | n/a
12 | 24 |  | 12 | CTD deployment
13 | 25 |  | n/a | n/a
13 | 26 |  | 13 | Plot data from test
14 | 27 |  | n/a | n/a
14 | 28 |  | 14 | Plot data from test
15 | 29 |  | n/a | n/a
15 | 30 |  | 15

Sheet: Assigments, Quizzes
Assignment | Week
1 | 1 | Name 5 platforms used for ocean observing and what sensors they may have
2 | 2 | What is UART / I2C / RS232 / RS484? Benefits and trade-offs of each (matrix?). What is an integer, float, etc., and when to use
3 | 4 | Everything you need to know to integrate the salinity sensor (data sheet, communication protocol, and example code)
4 | 7 | Data plotting from bench test
5 | 9 | Show your parents what you make in lab and explain how it works (in person, via video, etc.). How did they react and what were their thoughts?
Quiz
1 | 1 | What is an embedded system? What do you think this class is? What do you hope to gain out of this class and learn by the end of the semester?
2 | 2 | What is a CTD and what are they used for? Have all sensor data sheets downloaded and know where
3 | 5 | Temp and salinity sensor, sd card, and microcontroller
4 | 7 | Bench test quiz - successfully test on the bench, verbally tell me what each part is and what it does
Exam
1 | 8 | Cumulative so far
Final
1

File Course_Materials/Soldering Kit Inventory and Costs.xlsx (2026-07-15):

 | What | Cost Per | Num | Cost | Link
Tools | Soldering iron | $20.0 | 1 | $20.0 | https://www.adafruit.com/product/3685 | . | OR
 | Soldering iron stand | $8.0 | 1 | $8.0 | https://www.amazon.com/Soldering-Spring-Holder-Support-Station/dp/B08JLJLX4D | . | https://www.amazon.com/Weller-Digital-Soldering-Station-WE1010NA/dp/B077JDGY1J?crid=243Z2OCPATJRL | .
 | Soldering Iron tip cleaner | $10.0 | 1 | $10.0 | https://www.amazon.com/Kaisiking-Soldering-Iron-Cleaner-Solder/dp/B0CNVS7BFZ?crid=1GX1974XKOUS6 | . | Better one that comes with stand
 | Flush diagonal cutters | $7.2 | 1 | $7.2 | https://www.adafruit.com/product/152 | . | but it costs $115
 | 20-30 AWG Wire Strippers | $17.5 | 1 | $17.5 | https://www.adafruit.com/product/527 | .
 | Self-Adjusting Wire Strippers | $12.0 | 1 | $12.0 | https://www.adafruit.com/product/4747 | .
 | Simple pliers | $3.0 | 1 | $3.0 | https://www.adafruit.com/product/146 | .
 | Solder sucker | $5.0 | 1 | $5.0 | https://www.adafruit.com/product/148 | .
 | Half-size breadboard | $5.0 | 2 | $10.0 | https://www.adafruit.com/product/4539 | .
 | Helping hands | $27.0 | 1 | $27.0 | https://www.amazon.com/KOTTO-Soldering-Magnetic-Flexible-Workshop/dp/B07W42SR65 | .
 | Fume extractor | $70.0 | 1 | $70.0 | https://www.amazon.com/dp/B07HPZ3FF6 | .
 | Digital multimeter | $18.0 | 1 | $18.0 | https://www.adafruit.com/product/2034 | .
 | Safety glasses (x12) | $15.0 | 1 | $15.0 | https://www.amazon.com/TICONN-Clear-Safety-Glasses-Pack/dp/B0BGSFQJF6 | .
 | Desktop power supply | $50.0 | 1 | $50.0 | https://www.amazon.com/Adjustable-Switching-Regulated-Adjustments-Jesverty/dp/B09YSJQWRG | .
Consumables | Solder | $27.5 | 2 | $55.0 | https://www.adafruit.com/product/1930 | .
 | Tip rinner | $6.5 | 1 | $6.5 | https://www.amazon.com/Thermaltronics-FBA_TMT-TC-2-Lead-Tinner-Container/dp/B00NS4J6BY | .
 | Solder Wick | $3.0 | 2 | $6.0 | https://www.adafruit.com/product/4456 | .
 | Liquid Flux Pen | $8.0 | 2 | $16.0 | https://www.adafruit.com/product/3468 | .
 | Heat Shrink | $5.0 | 3 | $15.0 | https://www.adafruit.com/product/1649 | .
 | Polyimide Tape | $5.0 | 2 | $10.0 | https://www.adafruit.com/product/3057 | .
 | Hook-up Wire Spool Set | $30.0 | 1 | $30.0 | https://www.adafruit.com/product/3175 | .
 | 100K ohm Resistors (x25) | $1.0 | 4 | $4.0 | https://www.adafruit.com/product/2787 | .
 |  |  |  | $415.2 | TOTAL

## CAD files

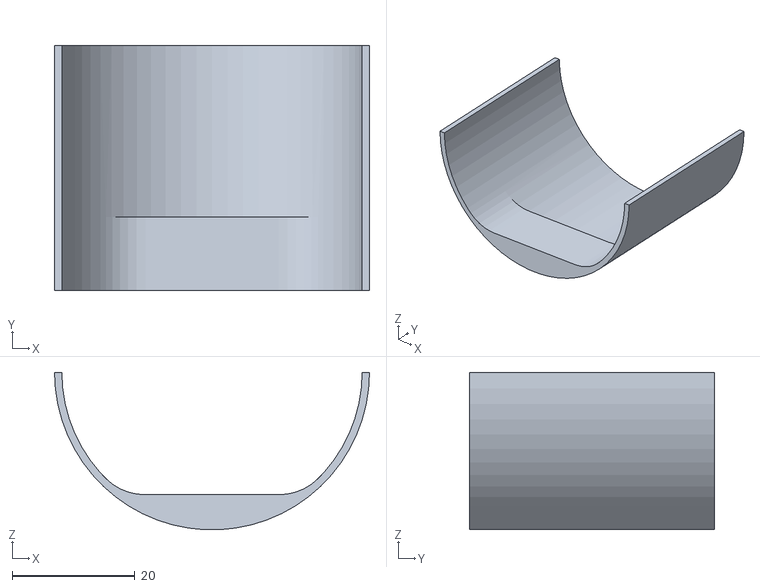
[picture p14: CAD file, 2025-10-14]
CAD_FIles/2in_tray_extender_for_switch_print1.STL
51.4 x 40.0 x 25.7

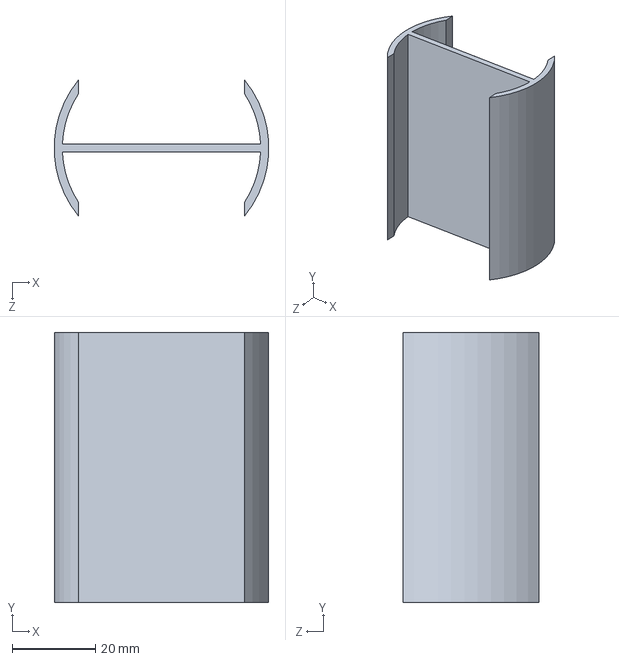
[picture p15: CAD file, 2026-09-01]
CAD_FIles/solidworks/2in_sensor_tray.SLDPRT
51.6 x 65.0 x 32.8 mm

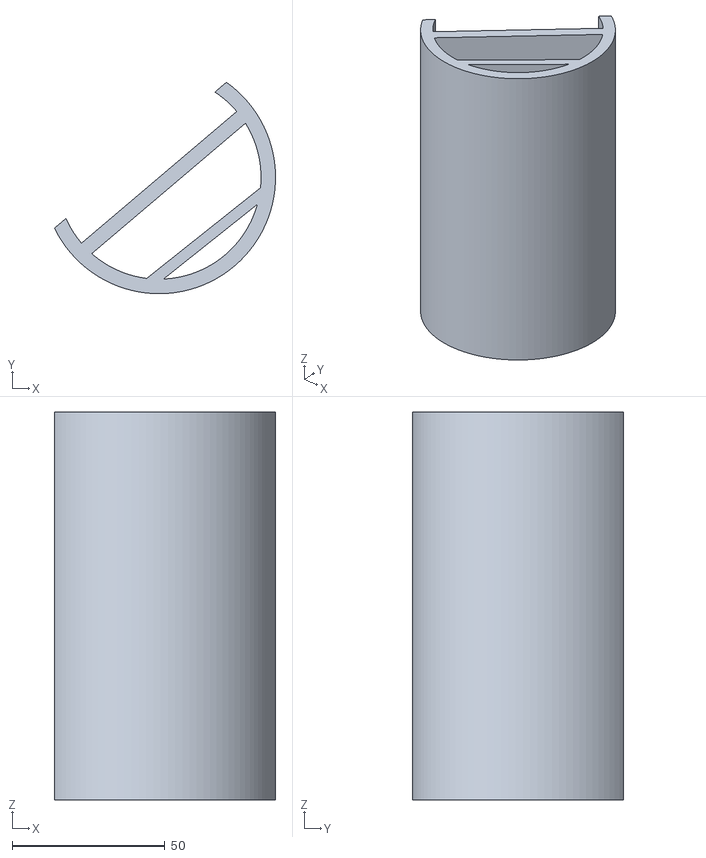
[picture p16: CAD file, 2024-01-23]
z_v1/SeaLabCTD_v1/b_3d_printed_parts/CTD2020 Smoother Sides STL.stl
72.4 x 69.2 x 127.0

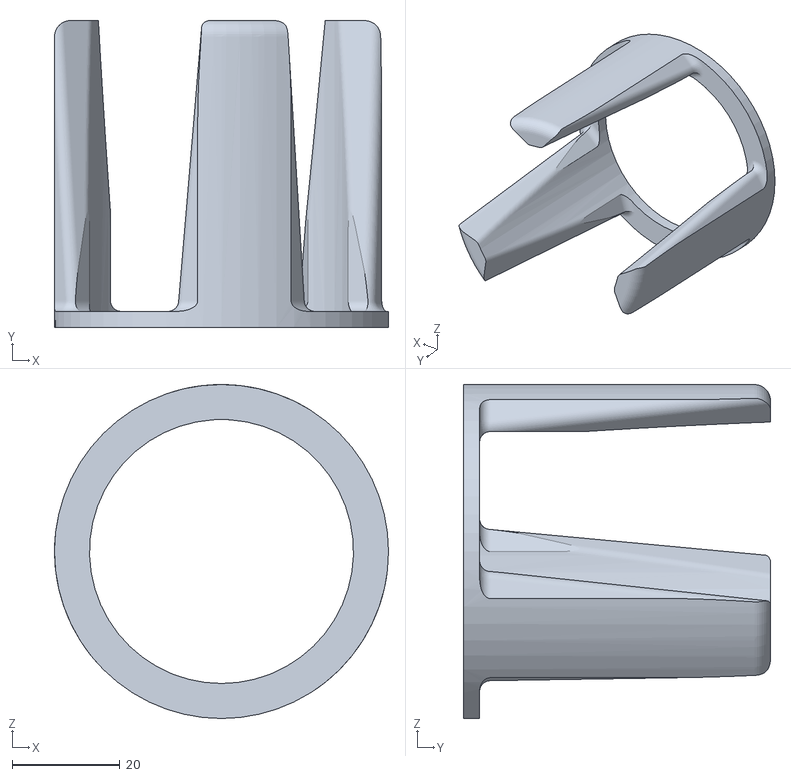
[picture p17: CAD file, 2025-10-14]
CAD_FIles/protector_tongs_print1.STL
62.0 x 57.0 x 62.0

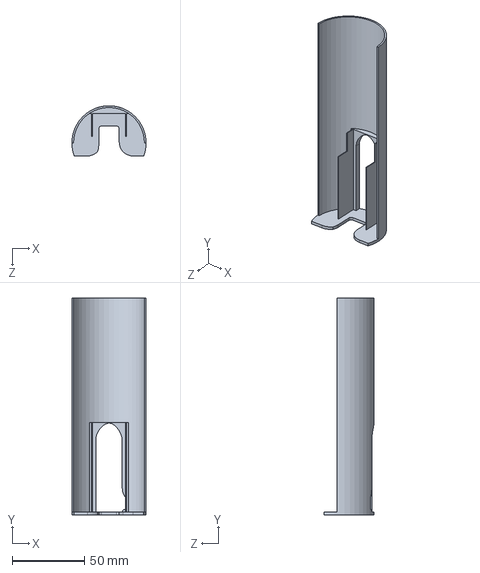
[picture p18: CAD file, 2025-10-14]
CAD_FIles/solidworks/2in_datalogger.SLDPRT
51.4 x 150.0 x 34.9 mm

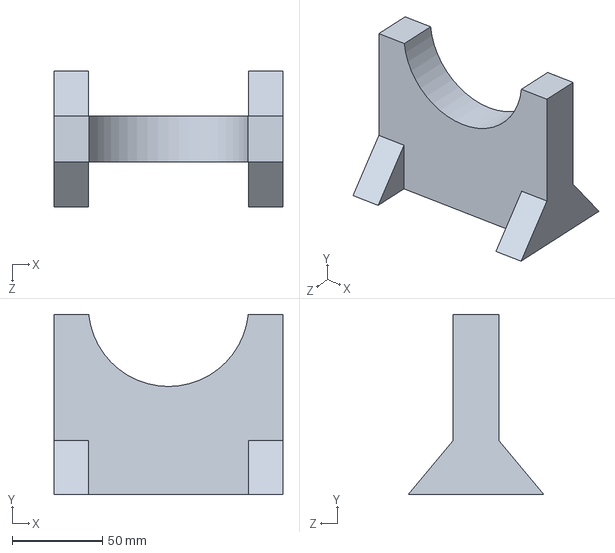
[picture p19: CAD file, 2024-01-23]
z_v1/SeaLabCTD_v1/b_3d_printed_parts/Housing Holder.SLDPRT
127.0 x 100.0 x 75.4 mm

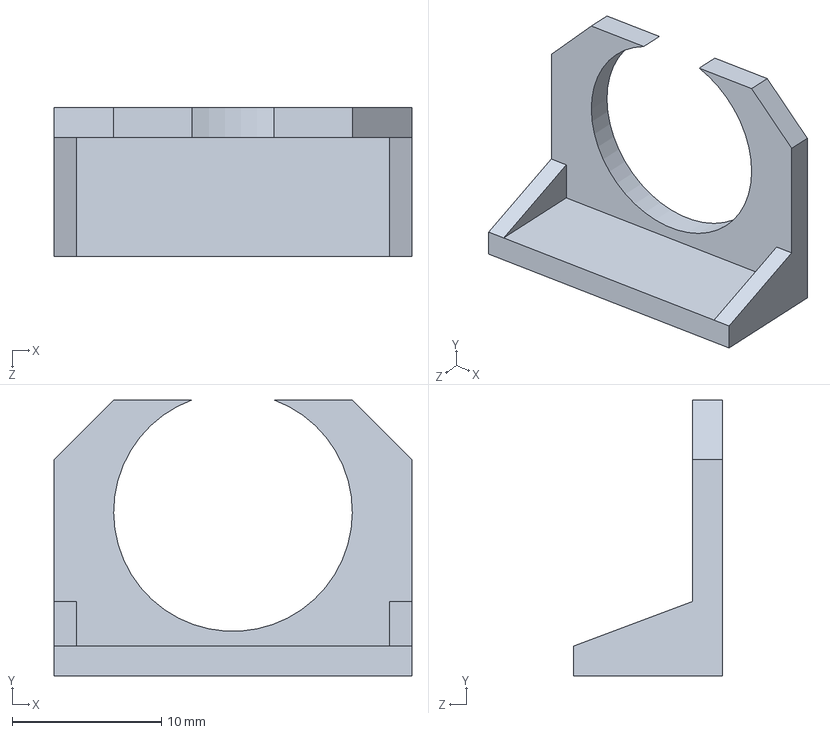
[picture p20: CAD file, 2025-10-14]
CAD_FIles/solidworks/switch_holder.SLDPRT
24.0 x 18.5 x 10.0 mm

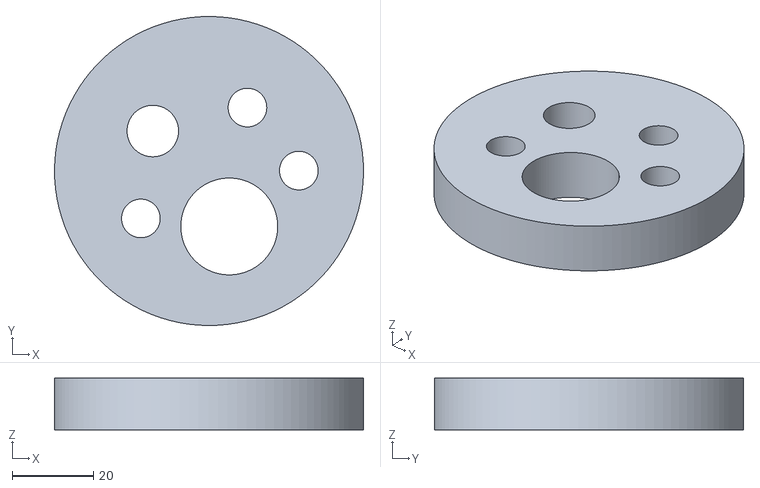
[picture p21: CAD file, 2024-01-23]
z_v1/SeaLabCTD_v1/b_3d_printed_parts/end_cap.stl
76.2 x 76.2 x 12.7

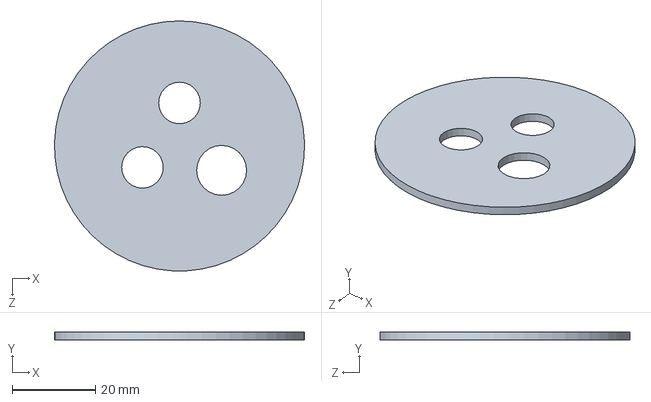
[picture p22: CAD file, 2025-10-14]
CAD_FIles/solidworks/2in_sensor_drill_area.SLDPRT
60.1 x 2.00 x 60.1 mm

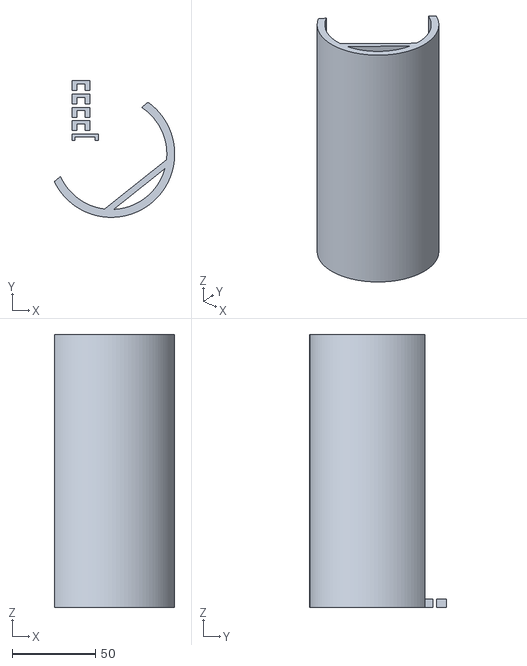
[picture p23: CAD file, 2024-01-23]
z_v1/SeaLabCTD_v1/b_3d_printed_parts/small part holders.stl
72.4 x 82.1 x 164.0

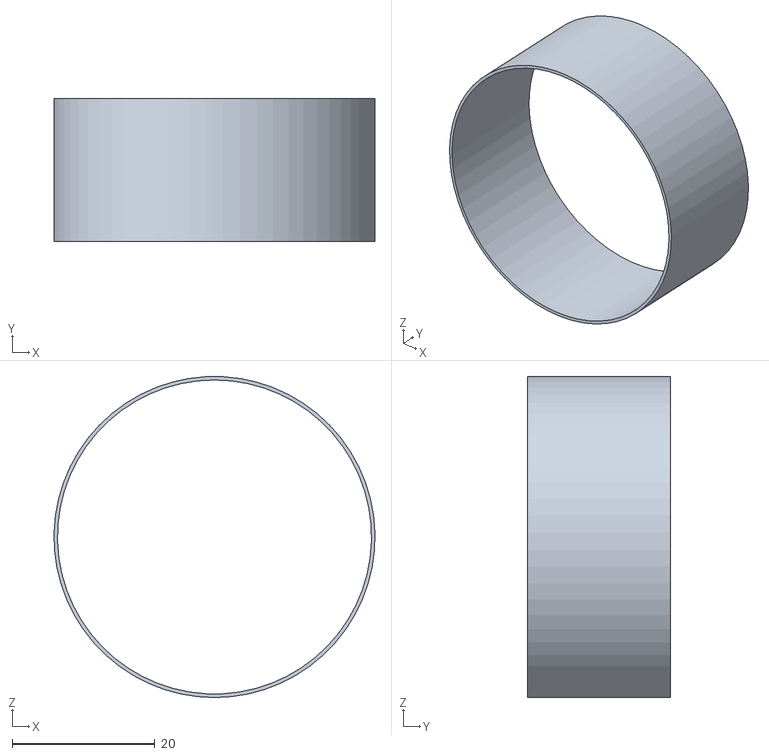
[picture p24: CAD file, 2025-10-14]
CAD_FIles/epoxy_ring_print1.STL
45.0 x 20.0 x 45.0

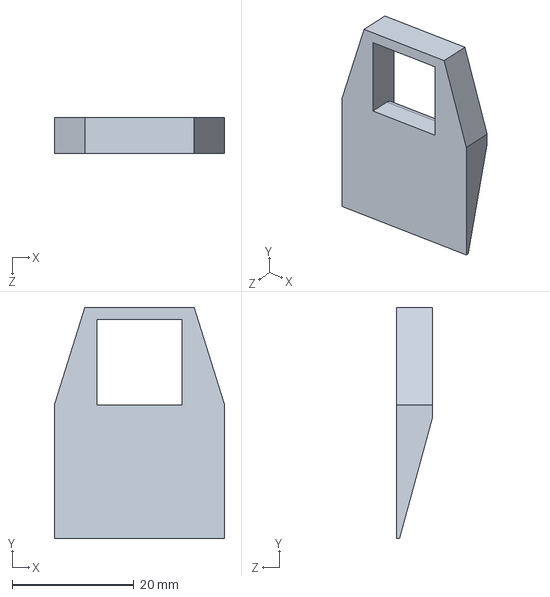
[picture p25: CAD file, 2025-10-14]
CAD_FIles/solidworks/handle.SLDPRT
28.0 x 38.0 x 6.00 mm

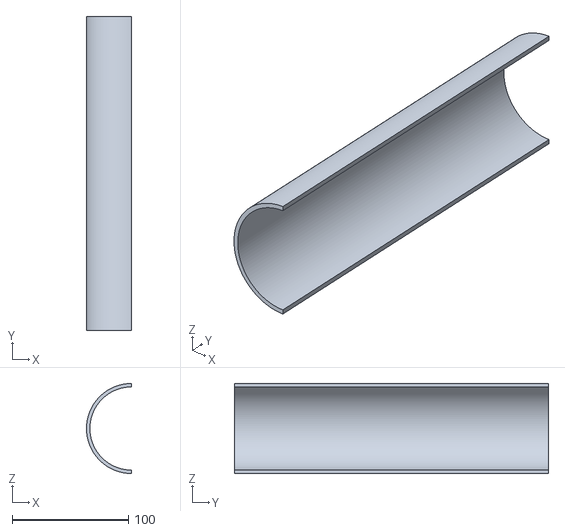
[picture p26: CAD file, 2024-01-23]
z_v1/SeaLabCTD_v1/b_3d_printed_parts/big tray smaller.STL
38.7 x 270.0 x 77.5

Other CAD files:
CAD_FIles/switch_holder_print1.STL
CAD_FIles/2in_datalogger_tray_print1.STL
CAD_FIles/2in_sensor_drill_area_print3.STL
CAD_FIles/solidworks/2in_tray_extender_for_switch.SLDPRT
z_v1/SeaLabCTD_v1/b_3d_printed_parts/tray.stl
CAD_FIles/2in_sensor_tray.STL
CAD_FIles/2in_tray_joiner_print2.STL
CAD_FIles/handle_print1.STL
CAD_FIles/inside_washer_print2.STL
CAD_FIles/solidworks/2in_tray_joiner.SLDPRT
CAD_FIles/solidworks/epoxy_ring.SLDPRT
CAD_FIles/solidworks/inside_washer.SLDPRT
CAD_FIles/solidworks/protector_tongs.SLDPRT
z_v1/SeaLabCTD_v1/b_3d_printed_parts/CTD2020 SMOOTHER SIDES.skp
z_v1/SeaLabCTD_v1/b_3d_printed_parts/CTD2020 end cap.skp
z_v1/SeaLabCTD_v1/b_3d_printed_parts/CTD2020.skp
z_v1/SeaLabCTD_v1/b_3d_printed_parts/EC holder.SLDPRT
z_v1/SeaLabCTD_v1/b_3d_printed_parts/EC holder.STL
z_v1/SeaLabCTD_v1/b_3d_printed_parts/Flange Holdy-Bit.SLDPRT
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

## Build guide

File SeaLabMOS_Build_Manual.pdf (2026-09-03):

# SeaLabMOS

# Modular Oceanographic Systems

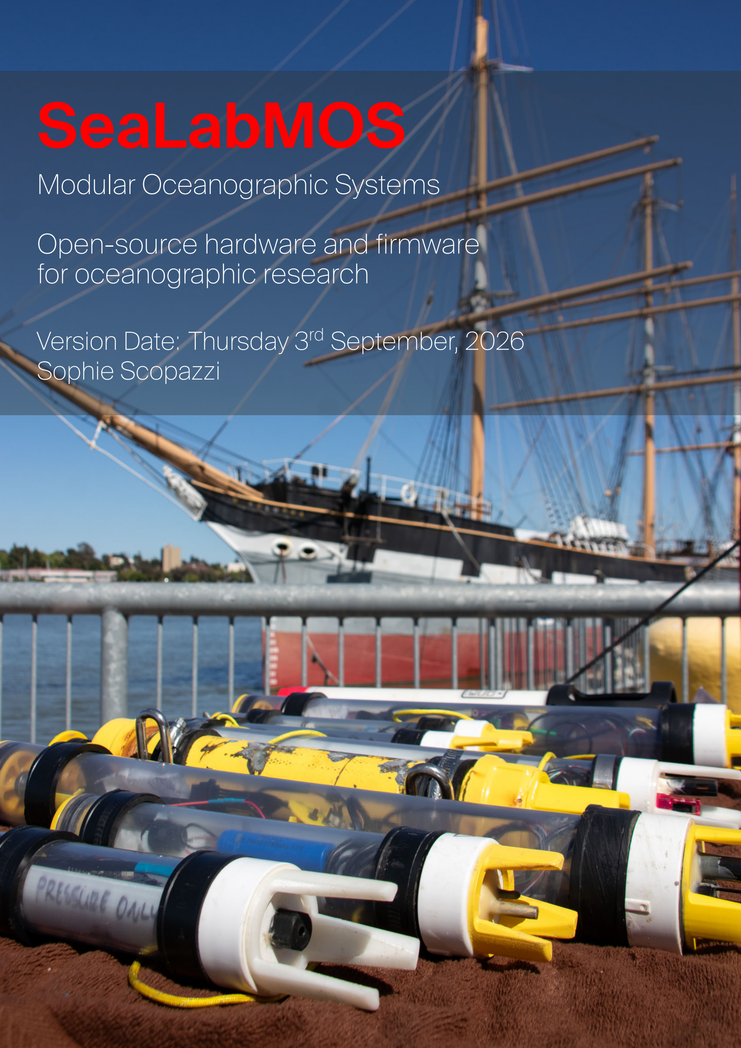
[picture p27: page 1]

# Open-source hardware and firmware for oceanographic research

# Version Date: Thursday 3rd September, 2026 Sophie Scopazzi

# Contents

Preface | iii
1 Ocean Sampling Background | 1
2 Base Hardware Components | 4
3 Sensors | 8
4 Default Builds | 15

ii

# Preface

This manual remains a work in progress. Please look at version date below.
If you have experience with oceanographic sampling systems/methods, I recommend skipping to chapter 2. If you only want the wiring instructions, see chapter 3
If you have any questions, please reach out to me!
– Text: 707-520-4460
– Email: aspectwave@pm.me
– IG: sophiescopazzi
– LinkedIn: Sophie Scopazzi (https://www.linkedin.com/in/sophie-scopazzi/)

Version Date: Thursday 3rd September, 2026 Sophie Scopazzi

## 0.1. SeaLabMOS System Configurations

The system has been designed with two operational methods in mind: profiling and static. As the SeaLabMOS family of systems are designed to be modular, each depoyment method has different sensors that better suit each type. When looking at the following table think about the science questions you are attempting to answer.
1. What do you want to sample (temperature, salinity, location)
2. How deep do you you want to sample?
3. Do you want to see live data at the surface or at depth?
4. How long will the system be deployed for (the desired endurance)?

Table 1: SeaLabMOS Deployment Types and Platforms

Profile | Static | Live View
1.5 in PVC RP2040 – RTC OLED Switch 2.2 Ah – Salt BR Temp BR Bar30 – – – 140m | 2 in PVC RP2040 – RTC OLED Switch 4.4 Ah – Salt BR Temp BR Bar30 Thermistor DS18B20 – 140m | 2 in Steel RP2040 – RTC OLED Switch 4.4 Ah – Salt BR Temp BR Bar100 Thermistor DS18B20 – 350m | Bottom Pressure Recorder 1.5 in PVC RP2040 – RTC – Switch 4.4 Ah – – – BR Bar02 – – – 140m | Temperature Logger 1.5 in PVC RP2040 – RTC – Switch 2.2 Ah – – – – Thermistor DS18B20 – 140m | Surface Nalgene RP2040 GNSS (option) RTC/GNSS – Switch 4.4, 6.6, 10 Ah Solar (option) Salt – – Thermistor DS18B20 Orange LED 2m | Wired Profile Pelican case Raspberry Pi GNSS GNSS Time Screen 12 V to 5 V – – Salt BR Temp BR Bar30 Thermistor DS18B20 – 140 m–350m

iii

# List of Figures

1.1 200 meter cast of the two-inch steel SeaLabMOS CTD | | 1
1.2 Temperature–Salinity (TS) diagram of the same data as in Fig. 1.1 | | 2
2.1 Calculated X and Y for 590 nm [luxalight_cie_convertor] | | 7
3.1 Resistors for voltage measurement and small wire for RTC interrupt | | 8
3.2 Placeholder image - not the best | 10
3.3 Placeholder image - do not have one | 10
3.4 The two different connectors. White is what must be cut off and black is what it is exchanged for 11 3.5 Wide photo of Blue Robotics’ temperature sensor wiring. Note heat shrink on wires before
soldering wires together | 12
3.6 Close photo of Blue Robotics’ temperature and pressure sensor wiring | 13
3.7 Photo of thermistor wiring. White wire goes to Feather’s analog port | 13
4.1 Smooth on the left, new on the right | 15
4.2 The washer should snap into place so do not push it all the way in until you place the Superglue
under it | 16
4.3 The end cap in the vice of a drill press. Even if/when the drill guide moves, it can break and the
drill/end cap orientation does not change | 16
4.4 Partly screwed into the PVC from the outside | 17
4.5 Bolting into place from the back | 17
4.6 The tolerances are tight, so do not be afraid on slightly rounding the corners | 17
4.7 Smooth on the left, sanded on right | 18
4.8 The ring stays in place forever now | 18
4.9 The top of the sensor face before epoxy. Glue the 3D printed tongs down with Superglue then
put in epoxy like on the back | 19
4.10 The end cap ready for bench testing after epoxy on both sides | 19
4.11 Here the wiring is at the top and the short connectors on the bottom are not cut; cut the short ones and solder to the long ones. The tray joiners are immediately to the left of the battery.
Under the switch is the handle | 20
4.12 Note cut red wire and intact black wire from connector top right | 20
4.13 The back of the sensor tray after the Atlas Scientific carrier board was bolted into place, before
the 5 port hub was added | 21
4.14 The Atlas Scientific carrier board in place | 21
4.15 Two CTDs ready for bench testing before glueing the end cap into the PVC pipe | 22

iv

1

# Ocean Sampling Background

Chapter Concepts:
1. What are different types of oceanographic sensor platforms and what are they used for?
2. How are research platforms typically deployed?

## 1.1. What is a CTD?

CTD (for Conductivity, Temperature, and Depth) refers to the three primary parameters measured by the instrument. Salinity is not measured directly but sampled with a conductivity sensor then calculated using the in-situ tvertical emperature and pressure. Data from a CTD can be used to plot salinity and temperature profiles as a function of depth. An example of what this can look like is Fig. 1.1.

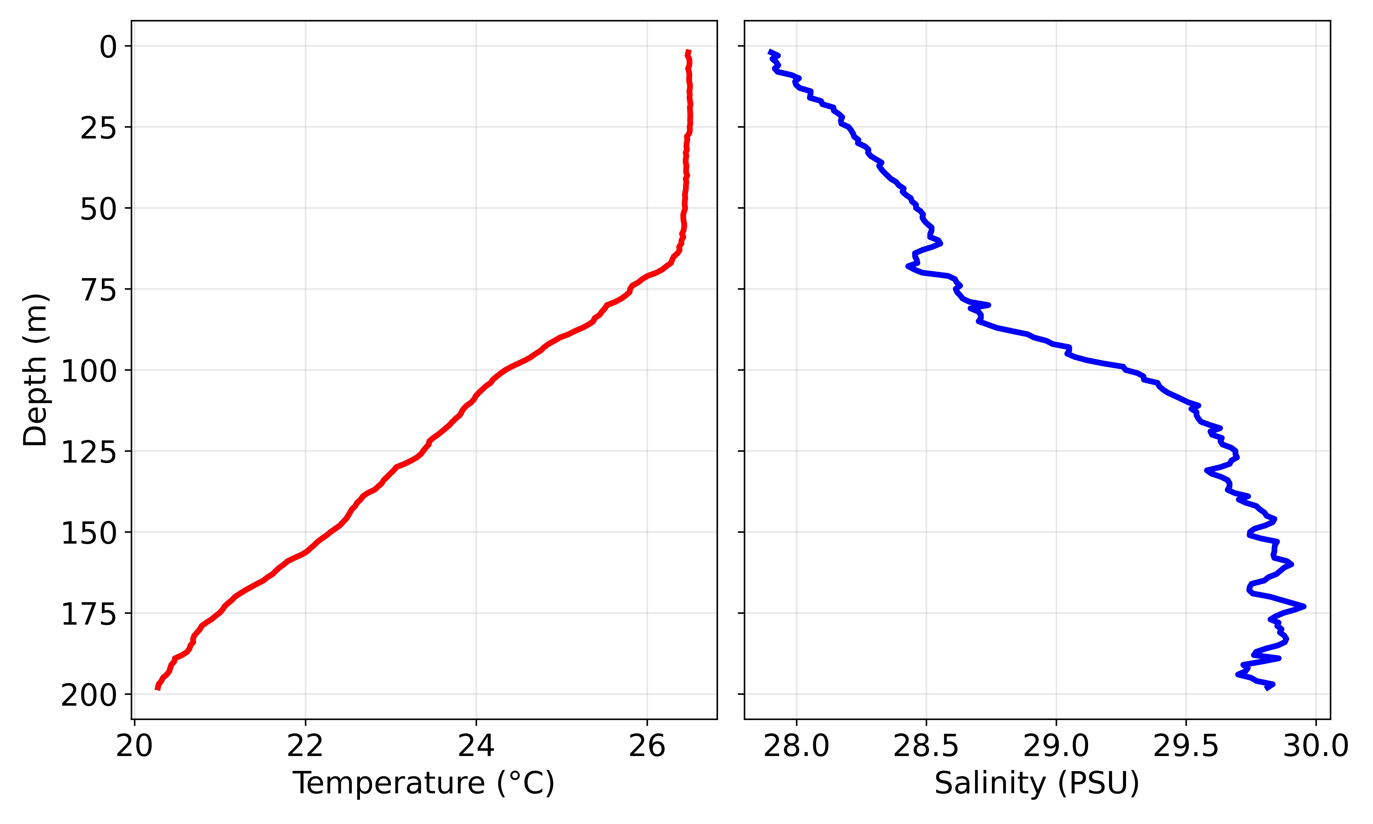
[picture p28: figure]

Figure 1.1: 200 meter cast of the two-inch steel SeaLabMOS CTD

1

1.2. CTD Applications | 2

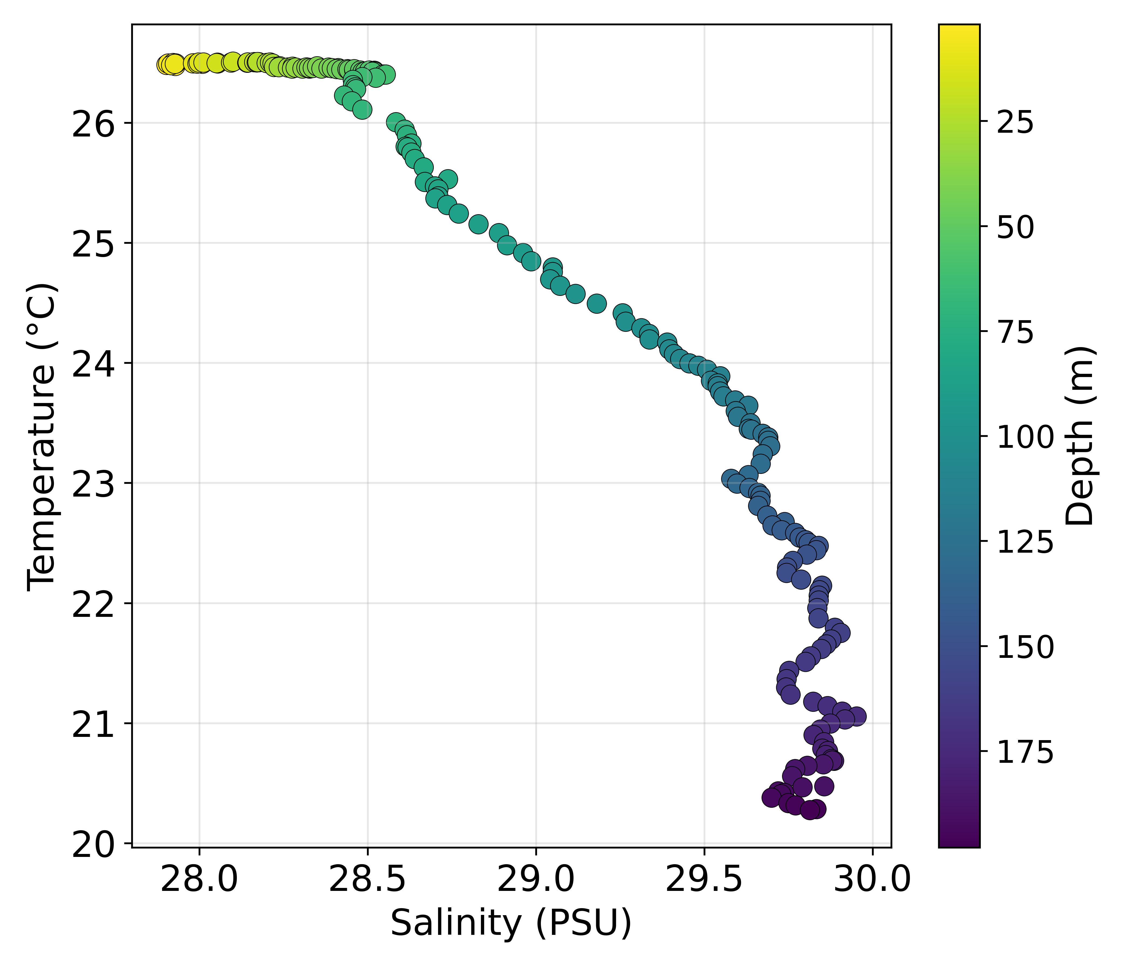
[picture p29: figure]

Figure 1.2: Temperature–Salinity (TS) diagram of the same data as in Fig. 1.1

Another common method to display CTD
data is called a TS diagram (short for temperature-salinity) because the plot compares the two variables, typically using color to indicate depth. Fig. 1.2 shows that the surface water was warmer and less salty, with temperature decreasing and salinity increasing with depth.

## 1.2. CTD Applications

CTD data can be used to answer questions such as whether the water column is stable and resistant to vertical mixing or unstable and prone to mixing, and to determine the depth of the thermocline or halocline. This information also assists with further study of the micro-organisms in the epipelagic zone, the upper photic layer of the ocean where sunlight penetrates.

Another important application of CTD
data is calculating the speed of sound
through the water column, as water temperature and salinity effect the density of seawater, which directly effects sound propagation through the medium. The variation in water density and temperature bend or reflect sound waves, making this also important information for areas of naval warfare such as detection range and target location accuracy. Beyond these applications, understanding sound propagation in the water column is critical for underwater communication systems, environmental monitoring, and scientific surveys, where accurate acoustic measurements are necessary for multi-beam sonar mapping of the seafloor.

## 1.3. How CTDs are deployed

Generally speaking, a oceanographic research platform can be deployed dynamically or statically. A system can be...
1. Lowered from the surface to vertically profile a column of water, typically called a cast. It could also be affixed to a system that traverses the water column up and down (a winch, wire walker, ocean glider, Argo float, etc.).
2. Affixed to a surface buoy, pier, anchored to the sea floor, or other similarly static location.
3. On a drifting surface float.

Each deployment type has different design considerations, sensor selection, and resulting cost trade-offs. For example, a stationary moored system can be powered via a cable with power-hungry sensors with a fast swample rate, while a mobile profiling float prioritizes compactness, low weight, and energy-efficient data logging. When it comes to sampling the ocean, there are many possible system configurations, ranging from simple single-parameter sensors to fully integrated, multi-sensor platforms capable of measuring temperature, salinity, dissolved oxygen, turbidity, and more. Each configuration presents trade-offs in terms of data resolution, deployment duration, maintenance requirements, and overall cost, meaning the choice of system must align closely with the scientific goals, operational constraints, and environmental conditions of the deployment.

## 1.4. Temperature Loggers

Uses:
– Monitor marine heatwaves and long-term climate trends.
– Characterize thermal stratification and mixing in the water column.

1.5. Bottom Pressure Recorder | 3

– Support habitat studies for corals, kelp, and fish.
– Provide baseline environmental data for impact assessments.
– Validate ocean models and satellite sea-surface temperature products.

## 1.5. Bottom Pressure Recorder

Uses:
– Measure water level changes for tidal and tsunami monitoring. – Track long-term sea-level rise in coastal and deep-ocean sites.
– Observe internal waves, storm surges, and barotropic currents.
– Support calibration of numerical ocean circulation models.
– Provide reference pressure data for moorings and CTD deployments.

## 1.6. Surface Float

Uses:
– Sample the surface ocean for temperature, salinity, etc., while also potentially carrying meteorological sensors such as wind, temperature, air pressure, and humidity.
– Keep moorings vertical and help maintain sensor depth.
– Provide surface visibility and recovery aids for systems that are deployed underwater.
– Support GPS, Iridium, or LoRa telemetry packages for real-time data.
– Act as platforms for surface drifters or wave-measurement systems.

2

# Base Hardware Components

Chapter Concepts:
1. Sensor selection considerations.

## 2.1. Microcontroller Selection and Base System

The SeaLabMOS main board is the Adafruit Feather RP2040 Adalogger - 8MB Flash with microSD Card. (https://www.adafruit.com/product/5980) It has an onboard microSD card slot, battery charging capability, and STEMMA QT port for solderless sensor integration. The RP2040 microcontroller has the capability to be overclocked for additional performance and underclocked for additional power savings when endurance is paramount.

Many types/brands of microcontroller could be used, so long as they have an I2C bus and UART capability. Alternatives that may work include:
– Arduino Uno R3 / Adafruit Metro 328. Only fits in larger enclosures and does not have a built in microSD card, but has many shield options. Could be good for bench testing.
– Adafruit QT Py RP2040 (Product ID: Product ID: 4900¹ (https://www.adafruit.com/product/4900)
) with Adafruit LiIon or LiPoly Charger BFF Add-On for QT Py (Product ID: 5397² (https://www.adafruit.com/product/5397)
). Extremely small with no built in microSD card. – Teensy 4.1³ (https://www.pjrc.com/store/teensy41.html)
. Small and powerful. Probably overkill for the current SeaLabMOS use-case unless adapting this work into something more computationally intensive.

The required base parts of the SeaLabMOS are listed in Table 2.1. The OLED display with buttons, GP-S/GNSS, and beacon are mission specific and used when needed, resulting in a cost range:
– $45 no screen
– $60 with screen
– $90 with Mini GPS for location
– $111.5 with Ultimate GPS for location w/ external antenna

## 2.2. Firmware

The firmware is the same for all versions of the SeaLabMOS family of systems. The sensors are selected by boolean values in the main .ino file as defined in GitHub⁴ (https://github.com/sscopazzi/SeaLabMOS)

### 2.2.1. Default Record Format for Comma-Separated-Values

Due to the variable nature of SeaLabMOS, a default header format is used across all firmware. Each firmware type updates only the relevant attached sensor values while leaving the others untouched, and the nthe CSV is only populated by the updated values. In this manner, post-processing of data (or live data processing, if building a tethered system) is standardized with one data-ingestion header format.

1https://www.adafruit.com/product/4900
2https://www.adafruit.com/product/5397
3https://www.pjrc.com/store/teensy41.html4https://github.com/sscopazzi/SeaLabMOS

4

2.3. Endurance and Power Monitoring | 5

Table 2.1: Base Datalogger Hardware

Name | Adafruit Part # | What it does | Accuracy | Cost
Adafruit Feather RP2040 Adalogger w/ microSD SD/MicroSD Memory Card (512 MB) DS3231 Precision RTC FeatherWing CR1220 12mm 3 V Lithium Coin Cell Battery Lithium Ion Battery Pack 3.7 V 2.2 Ah (or 2.5–10 Ah) Adafruit FeatherWing 128×64 OLED display Mini GPS (PA1010D) Ultimate GPS Breakout (PA1616D) External Active GPS Antenna High-strength ’rare earth’ magnet STEMMA QT / Qwiic JST SH 4-pin Cable Stemma QT / Qwiic 5 Port Hub& 5625 (https://www.adafruit.com/product/5625) | 5980 (https://www.adafruit.com/product/5980) 5252 (https://www.adafruit.com/product/5252) 3028 (https://www.adafruit.com/product/3028) 380 (https://www.adafruit.com/product/380) 1781 (2.2 Ah) (https://www.adafruit.com/product/1781) 4650 (https://www.adafruit.com/product/4650) 4415 (https://www.adafruit.com/product/4415) 5440 (https://www.adafruit.com/product/5440) 960 (https://www.adafruit.com/product/960) 9 (https://www.adafruit.com/product/9) 5385 (https://www.adafruit.com/product/5385) Sensor Connection | Datalogger Data storage Real time clock Battery for RTC Battery Screen, Buttons GPS/GNSS, Time GPS/GNSS, Time For Ultimate Hold antenna Sensor Connection | — — ±2 minutes per year — — — 2 m, 10 Hz meters, 10 Hz accuracy | $15 $5 $14 $1 $10 $15 $30 $30 $21.5 $2.5 $1–1.5 $2.5

Note: Accuracy of RTC from manufacturer. GPS/GNSS module accuracy from testing.

### 2.2.2. Saving Data to the Onboard MicroSD Card

All data is indexed by time from the RTC and saved to the onboard microSD card as CSV, with newlines for each record. For dynamic systems, the firmware creates a new file at each power-on (e.g., 2025-07-10T14-22-17.csv), while the firmware for static systems for multi-day deployments creates one file per day (e.g., 2025-07-21.csv). The datetime format follows ISO 8601⁵
, with ”-” replacing ”:” to avoid forbidden filename characters.

Profile firmware at 200 MHz (5 Hz) produces 380–450 bytes/s (about 76–90 bytes/sample), filling a 256 MB card in 7–8 days. Static deployments sample far less frequently, so battery life, not file size, is the limiting factor. Using an 8 GB card removes storage concerns and smaller cards are feasible if sample duration is altered.

Saving to the onboard microSD restricts data access to post-deployment retrieval; live monitoring below the surface is not possible. Future wired version(s) of the SeaLabMOS are planned for real-time data monitoring of casts to depth.

## 2.3. Endurance and Power Monitoring

System endurance is highly variable, mostly due to the chosen battery. To assist in knowing what the battery voltage is upon system power-up, the following table is in the firmware to blink the Feather’s onboard NeoPixel. Section 3.1 contains the wiring information.

Table 2.2: Battery Voltage Ranges and Corresponding LED Colors
Voltage Range (V) | Color | Behavior | Description
≥ 4.00 3.80 – 3.99 3.60 – 3.79 3.40 – 3.59 3.35 – 3.39 < 3.35 | Green Cyan Yellow Purple Red Red | Solid Solid Solid Solid Solid Blinking | Fully charged Mostly full Moderate Low Critically low Dangerously low

### 2.3.1. Power Use of Each Component

This is difficult to measure without specialized equipment.

## 2.4. Real-Time Clock

For precise timekeeping, SeaLabMOS uses the DS3231 Precision RTC FeatherWing. The I2C-integrated Real Time Clock (RTC) fits right on top of the base board and has a Temperature Compensated Crystal

5
ISODates.

2.5. OLED Display | 6

Oscillator (TCXO) to help maintain accurate timing. The board also has a SQW/INT breakout pin, which is utilized to wake the microcontroller from a low-lower sleep mode.

## 2.5. OLED Display

If real-time data viewing, in-field pre-deployment button functionality and/or error message monitoring via text
is desired, SeaLabMOS can integrate the Adafruit FeatherWing OLED - 128x64 OLED⁶ (https://www.adafruit.com/product/4650) | . The OLED board
also has an extra STEMMA QT connector.

## 2.6. Location (GPS/GNSS)

If location of the start of the CTD cast is desired, or if building a surface asset, the Adafruit Mini GPS PA1010D⁷ (https://www.adafruit.com/product/4415) can be integrated through the STEMMA QT port. If this board is integrated into the system and used for location and time, the RTC may not be required. Alternatively, the GNSS board could be utilized for location and time and to set the RTC time before entering ”sleep mode” (the sensor datasheet terms it Backup Mode) to conserve power.

## 2.7. Flashing Yellow Lighted Beacon

In the SeaLabMOS underwater configuration an LED beacon is not needed; however, it should be considered for surface assets that will be deployed during hours of darkness and reduced visibility in areas where mariners or others on the water may come across the platform.

Table 2.3: Components Used for Yellow LED Beacon
Component | Specification / Description | Link
Amber (590 nm) Rebel LED on a SinkPAD-II with Side Emitting Optic | 74 lm @ 350 mA | luxeonstar.com⁸ (https://luxeonstar.com/product/sp-04-a8/)
350 mA BuckToot LED Driver – With Leads | Protects the LED | luxeonstar.com⁹ (https://luxeonstar.com/product/7027-D-350/)
Adafruit 12 V Bias Voltage Boost Converter – TPS61040 | Boosts 3.3 V from micrcontroller to 12 V for LED, has Enable pin for on/off | adafruit.com¹⁰ (https://www.adafruit.com/product/5644)

To maintain international standards for the safety of navigation, the International Association of Marine Aids to Navigation and Lighthouse Authorities (IALA) maintains standards for navigational beacons. SeaLabMOS systems, being a scientific device, is within the category of special marks requiring a yellow light. A light must be present during all times of darkness and reduced visibility (fog, smoke, etc.).

### 2.7.1. Color

The color of the light (590 nm) is important. As stipulated within Marine Signal Lights Colours E200-1 from December 2018 [iala_levels_g1038_2016], IALA strictly denotes the exact color of each light type. All “colours are specified with CIE 1931 standard colorimetric observer (2°-observer)’’ using Chromaticity Corner Coordinates (CCCs). The document indicates yellow using CCCs as stated in Table 2.4.
Table 2.4: IALA CCCs X and Y vs Nanometer Equivalent
| X | Y | Nanometer Equivalent
IALA Spec Calculated | 0.5865 0.5752 | 0.413 0.424 | ???.? (591.97) 590.0

The LED selected emits a wavelength of 590 nm, which falls within the yellow light specification required in Annex A, Color Regions.

### 2.7.2. Characteristic (Pattern)

As stipulated by IALA in 0110 Rhythmic Characters Of Lights On Marine Aids To Navigation¹¹, a special mark may only have certain characteristics. To simplify

6https://www.adafruit.com/product/4650
7https://www.adafruit.com/product/441511iala__characters_r0110_2021.

2.8. Light Sensors | 7

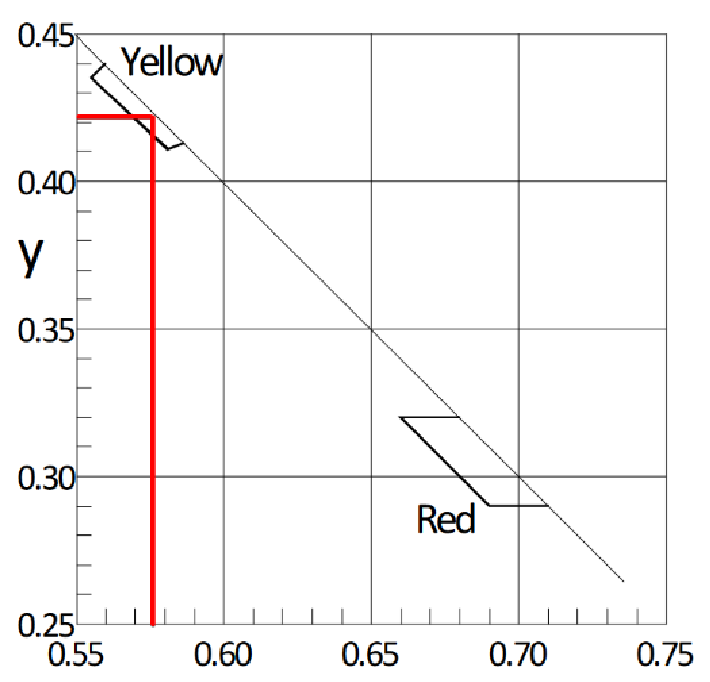
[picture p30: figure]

Figure 2.1: Calculated X and Y for 590 nm [luxalight_cie_convertor].

1. Group-occulting: This setting provides onlookers greater periods of light than darkness for easier identification. The IALA specification for special marks states “the number of eclipses in a group should not be greater than four in general, and should be five only as an exception”¹²
2. SeaLabMOS group-occulting: To better meet endurance needs and to help the LED not overheat, the flashing pattern is only shown once per minute (user configurable).

### 2.7.3. Automatic Timing of the Light

While “time switches, GNSS synchronization, [or] a real-time clock” can control light operation, the predominant method for night operation of AtoN lights is via photo-sensitive devices¹³. This allows automatic adaptability during poor visibility, such as fog. Care must be taken to select the correct ambient light switching level to minimize energy consumption and material wear. Ambient light levels (in lux) for different conditions are stated in the document’s Table 1, and astronomical events with associated lux are listed in Table 2 [iala_levels_g1038_2016].
In the current state of the SeaLabMOS, there is no light sensor integrated. We are investigating two options that could suit this use-case.
1. Adafruit TSL2591 High Dynamic Range Digital Light Sensor. (https://www.adafruit.com/product/1980)
2. Adafruit AS7262 6-Channel Visible Light / Color Sensor Breakout. (https://www.adafruit.com/product/3779)
While the light sensor could be used to control the beacon on a surface asset, we are also investigating the potential for light sensors to simulate PAR sensors.

## 2.8. Light Sensors

While the light sensor could be used to turn the LED beacon on and off, we are also investigating the potential for use as a low-cost PAR sensor.
– Adafruit TSL2591 High Dynamic Range Digital Light Sensor (Product ID: 1980). (https://www.adafruit.com/product/1980) Ultra low-light sensor with a wide dynamic range. I2C interface and STEMMA QT.
– Adafruit AS7262 6-Channel Visible Light / Color Sensor Breakout (Product ID: 3779). (https://www.adafruit.com/product/3779) Provides six discrete wavelength channels (450–950 nm). I2C communication and STEMMA QT.

This is slightly outdated, but Chapter 4 is currently the focus. If curious, research is ongoing. If you have any thoughts, suggestions, ideas, or other thoughts, please reach out!

12iala__characters_r0110_2021.
13iala_levels_g1038_2016.

3

# Sensors

## 3.1. Battery Voltage

Connect a 100KΩ resistor between BAT and A2 and a second 100KΩ from A2 to GND, following the power management instructions from Adafruit: https://learn.adafruit.com/adafruit-feather-rp2040-adalogger?view=all.

Table 3.1: Battery voltage divider connections

From | To
VBAT | Analog A2
Analog A2 | Ground

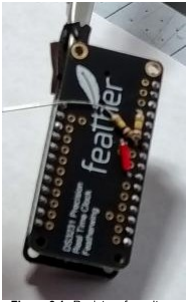
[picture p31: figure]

Figure 3.1: Resistors for voltage measurement and small wire for RTC interrupt

Voltage is measured using a resistor voltage divider connected to the Feather’s analog input pin as described by Adafruit¹
. The
Feather’s ADC measures a range of 0–3.3 V, so the voltage divider scales the battery’s max of 4.2 V down to a range compatible with the ADC. The divider consists of two resistors, R1 from the battery positive to the analog pin, and R2 from the analog pin to ground. The voltage at the analog pin is given by:

VADC = Vbat ·

R2
R1 + R2
where Vbat is the battery voltage. The ADC reading is then converted to an actual voltage by scaling the raw value to the 0– 3.3 V range of the ADC and then multiplying by the inverse of the voltage divider ratio. In the firmware, this is implemented as:

float v = analogRead(BATTV_PIN); // read ADC
v /= 4095.0; // convert to 0-1
v *= 3.3; | // scale to voltage at analog pin
v *= 2.0; | // undo 1:1 voltage divider

### 3.1.1. Voltage Correction Factor

Each system built will have a different system-specific correction factor that must be applied to account for individual resistor tolerances. This factor is determined empirically by comparing the feather’s voltage reading to a multimeter’s measurement. In the firmware this correction implemented within battMonitor.h as:

1adafruit_feather_rp2040.

| 8

3.2. Salinity: Atlas Scientific EZO-EC Embedded Conductivity Circuit and K1.0 Mini Probe | 9

#if SYSTEM_NAME == GREEN (for example)

v *= 1.053;

Steps to Find Correction Factor:
1. Ensure the Feather is printing the voltage to the serial monitor, for example with this program²
2. Measure from the positive wire of the battery (once you’ve wired up the power switch this should be easily accessible) to the Feather’s ground
3. Update the relevant SYSTEM_NAME’s correction factor
until the Feather matches the reading

For example, if the multimeter reads Vmm = 3.53 V and the Feather reads VFeather = 3.67 V, the correction factor can be calculated as
Correction factor =

VFeather

Vmm

=

3.67
3.53

≈ 1.043.

## 3.2. Salinity: Atlas Scientific EZO-EC Embedded Conductivity Circuit and K1.0 Mini Probe

The SeaLabMOS family uses the Atlas Scientific EZO-EC conductivity circuit with the Mini Conductivity K 1.0 kit³
to measure salinity via electrical conductivity. The EZO-EC circuit supports multiple output formats and is compatible with 3.3 V and 5 V systems, making it ideal for embedded applications. When paired with an accurate temperature sensor, this circuit allows real-time, in-situ salinity calculation using the Practical Salinity Scale (PSS-78).

### 3.2.1. Wiring

The EZO-EC circuit supports UART and I²C, but the SeaLabMOS uses UART for direct communication with the Feather RP2040 Adalogger wired as follows:

Table 3.2: Sensor to carrier board wiring

Module Pin | Feather
VCC | 3.3 V
GND | Ground
TX | RX (e.g., Serial1 RX)
RX | TX (e.g., Serial1 TX)
OFF | GPIO digital pin D4

Physically, this looks like using a 5-pin JST SM⁴ plug to make the datalogger tray capable of quick disconnection from the sensor tray. First, solder one end of the plug to the carrier board. Then, the other into the feather. Ensure you have the right orientation of the plug, because it can only plug in one way.

2https://github.com/sscopazzi/SeaLabMOS/tree/main/single_sensor_programs/vBatt_only3https://atlas-scientific.com/kits/mini-conductivity-k-1-0-kit/4https://www.adafruit.com/product/1664

3.2. Salinity: Atlas Scientific EZO-EC Embedded Conductivity Circuit and K1.0 Mini Probe | 10

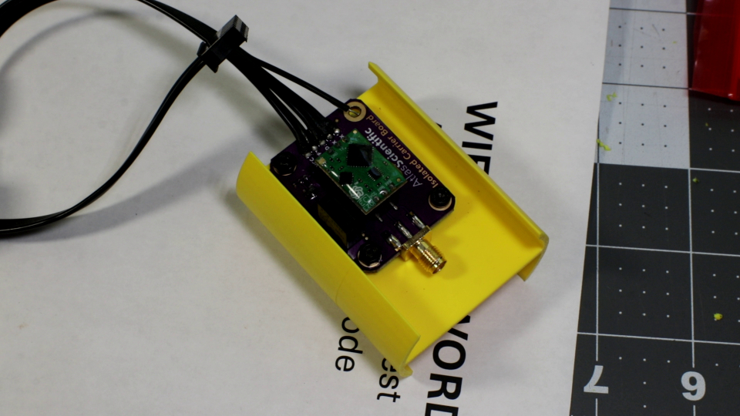
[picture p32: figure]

Figure 3.2: Placeholder image - not the best

For the feather side, start with one end of the plug’s wires. They will end up twisting at interesting angles to get situated. This might be the trickiest part of the soldering required so take your time.

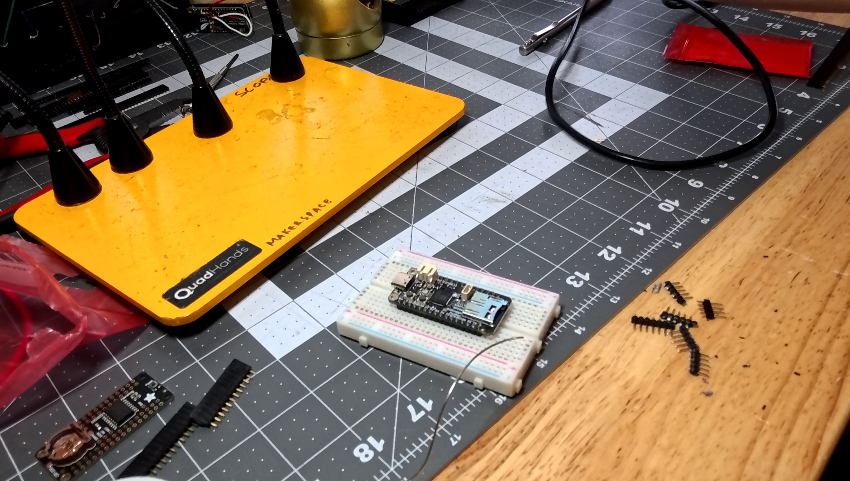
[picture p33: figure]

Figure 3.3: Placeholder image - do not have one

### 3.2.2. Calibration

By default on arrival, the EZO-EC should be configured for UART communication. If not, it can be configured for UART by sending the command I2C,0 over a temporary I²C connection, or by holding the EZO-EC’s PGM pad low on power-up for >10 seconds, which resets it to UART mode.

Once wired, it is possible to ”talk” with the EZO-EC circuit through the firmware and Arduino IDE. Once the Feather is wired to the sensor as above, it’s possible to send the commands listed in the EZO-EC datasheet⁵ (https://files.atlas-scientific.com/EC_EZO_Datasheet.pdf) .
The EZO-EC circuit supports one-, two-, or three-point calibration. For highest accuracy across a range of salinity, the SeaLabMOS uses the three-point calibration: dry, low, and high. Before calibrating the probe, set the temperature compensation value to the temperature reported by the Blue Robotics Fast Temp using the command:

RT,<value>\r

The carriage return (”\r”) is selected in the Arduino IDE and does not need to be manually typed. This will be used throughout the calibration process, which is as follows:
1. Dry Calibration:
– Remove the probe from all liquids and ensure it is thoroughly dry.

5https://files.atlas-scientific.com/EC_EZO_Datasheet.pdf

3.3. Temperature and Pressure Sensor Wiring | 11

– Once powered on, allow the probe to stabilize in air away from other electronics for 10–15 seconds. – Send Cal,dry via UART.
2. Low-Point Calibration:
– If wet and/or exposed or unknown previously, rinse the probe with distilled water and gently blot dry and/or blow dry with compressed air.
– Type, but DO NOT send, the command that you will send (e.g., Cal,low,12880).
– Immerse the probe in the low-point calibration solution (e.g., 12,880 µS/cm).
– Wait for readings to stabilize (usually about 5-10 seconds). You’ll notice that if left in the calibration solution for too long, the values will slowly drift. Send the calibration command once the value stabalizes, but before it drifts.
– Send the command Cal,low,<value> (e.g., Cal,low,12880).
3. High-Point Calibration:
– Rinse again with distilled water and blot the probe dry and/or blow dry with compressed air. – Type, but DO NOT send, the command that you will send (e.g., Cal,low,80000).
– Place it in the high-point calibration solution (e.g., 80,000 µS/cm).
– After readings stabilize, send Cal,high,<value> (e.g., Cal,high,80000).

Once complete, check the calibration status by sending Cal,?. A properly calibrated circuit will return the calibration points currently in use. If you followed the above, it will return 3.

### 3.2.3. Atlas-Scientific Power Management

To minimize power consumption during long deployments and when not actively sampling, the SeaLabMOS firmware turns the circuit on and off using GPIO Digital Pin 4.

## 3.3. Temperature and Pressure Sensor Wiring

Find the section that pertains to the sensors you have selected.

### 3.3.1. Blue Robotics Temp and Pressure

From Blue Robotics, the sensors has a 4-pos JST GH that is compatible with most flight controller boards, including Pixhawk and others (https://bluerobotics.com/store/sensors-cameras/sensors/bar30-sensor-r1/) (BM04B-GHS-TBT). (https://www.digikey.com/en/products/detail/jst-sales-america-inc/BM04B-GHS-TBT-LF-SN-N/807802) However, this connector is useless for our purposes. It must be cut off and replaced with a STEMMA QT / Qwiic JST SH 4-pin Cable. (https://www.adafruit.com/product/4210)

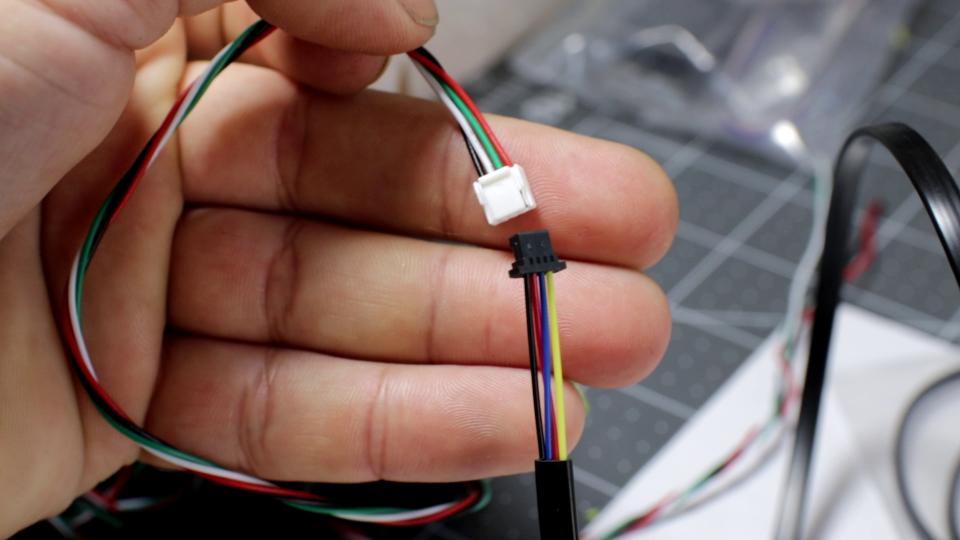
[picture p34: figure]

Figure 3.4: The two different connectors. White is what must be cut off and black is what it is exchanged for

Use the table below, or check the manufactures websites for which color is connected to what.

3.3. Temperature and Pressure Sensor Wiring | 12

Table 3.3: Blue Robotics to Adafruit STEMMA QT cables
Pin / Wire | Blue Robotics | Adafruit STEMMA QT
1 | Red – Vin | Red – V
2 | Green – SCL | Yellow – SCL
3 | White – SDA | Blue – SDA
4 | Black – GND | Black – GND

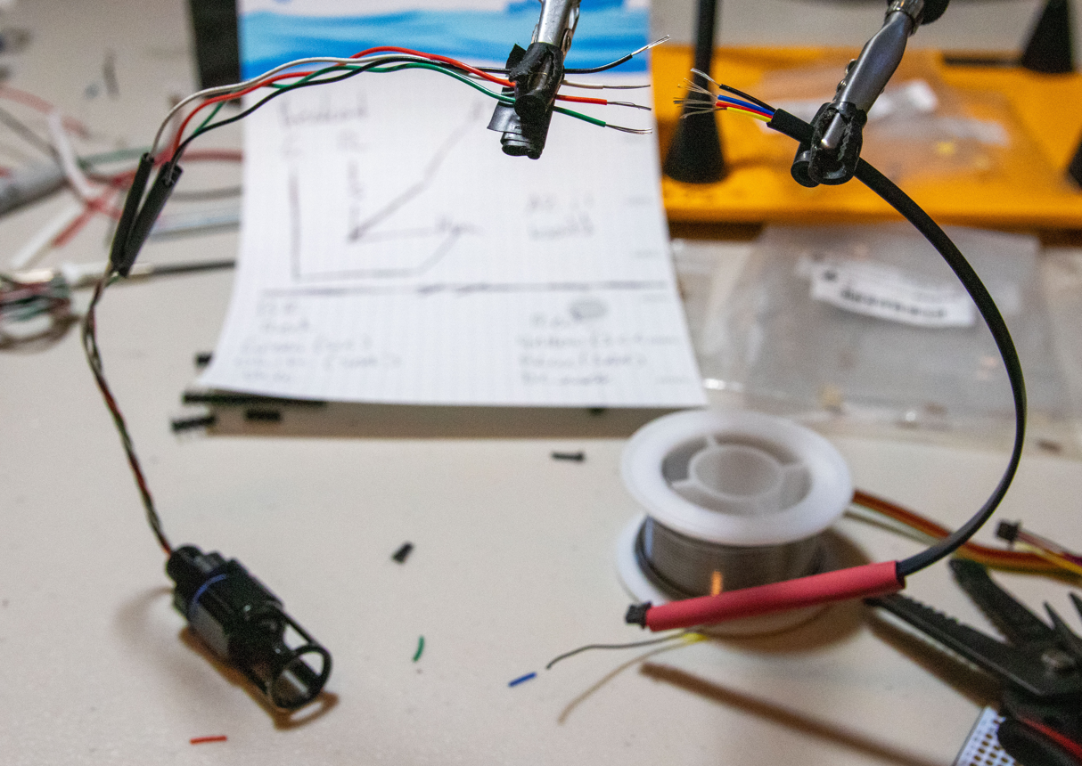
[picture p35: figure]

Figure 3.5: Wide photo of Blue Robotics’ temperature sensor wiring. Note heat shrink on wires before soldering wires together

3.4. Thermistor | 13

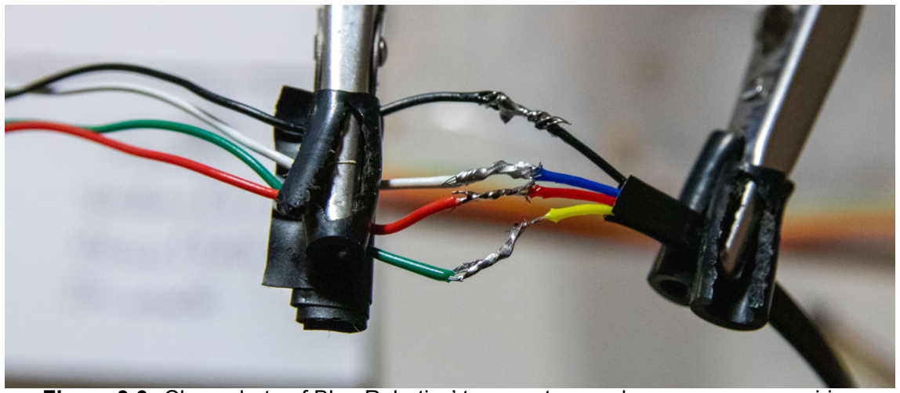
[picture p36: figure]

Figure 3.6: Close photo of Blue Robotics’ temperature and pressure sensor wiring

## 3.4. Thermistor

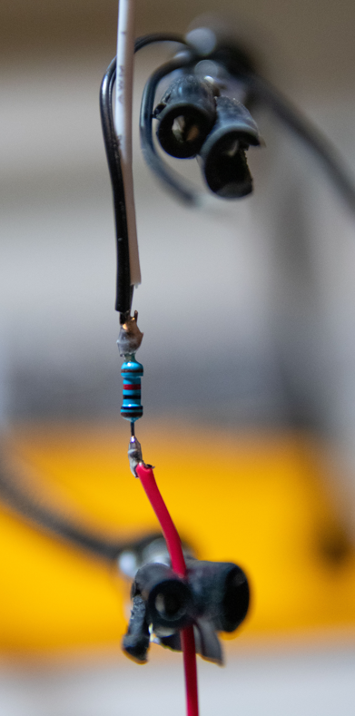
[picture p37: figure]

Figure 3.7: Photo of thermistor wiring. White wire goes to Feather’s analog port

The thermistor has two wires and comes with a 10 kΩ resistor. The sensor wire (white in the photo) is put on the thermistor side of the resistor that is connected to 3.7V power. Wiring is as follows:

Table 3.4: Thermistor wiring. Wire 1 and Wire 2 from the thermistor are interchangeable

Feather | Thermistor
A3 | Sensor wire (white in photo)
GND | Thermistor wire 1
3.3 V | Sensor wire and thermistor wire 2

### 3.4.1. Resistor Accuracy

The thermistor comes with a 10 kΩ resistor used in series; however, it is not perfectly 10 kΩ. To achieve the highest accuracy the resistor should be measured with a multimeter and the value in the firmware updated for the SYSTEM_NAME found within the firmware’s therm.h.

### 3.4.2. Analog to Digital Resolution

By default, the Feathers analog to digital converter (ADC) resolution is 10-bit with 1024 discrete levels. The Feather board does, however, have the capability for 12-bit resolution with 4095 discrete levels for greater accuracy. Setting the ADC resolution to 12-bit is specified in the firmware’s .ino file.

3.5. DS18B20 | 14

## 3.5. DS18B20

Please see the Adafruit resources. Will flesh out more here as time is available. https://www.adafruit.com/product/381https://www.adafruit.com/product/5971 https://learn.adafruit.com/adafruit-chainable-ds18b20-extender-breakout/pinouts

## 3.6. Bench Test Before Final Assembly

At this point, you should have:
1. The voltage resistors soldered in place
2. The interrupt wire from the RTC to the feather soldered in place
3. The Blue Robotics pressure sensor with a QWIIC connector instead of the one it came with
4. The Blue Robotics Fast Temp sensor with a QWIIC connector instead of the one it came with (or the other temperature sensor(s) you selected, like the thermistor or DS18B20)
5. The Atlas Scientific probe and carrier board, if using the salinity sensor
(1), (2) , and (3)
The next step is bench testing the system, before gluing everything into place.

4

# Default Builds

You will need the following equipment
1. Superglue
2. 9.5 mm and 12 mm drill
3. Small adjustable wrench
4. More things

## 4.1. 1.5in or 2.0in PVC

3D print all parts in the CAD files section of the GitHub page. Follow the filenames for how many of each to print.

### 4.1.1. End Cap

1. (optional) Sand the 3D printed protected tongs smooth, clean of dust, then spray paint your color of choice. Bright colors (yellow, pink) stand out more in the water (no photo yet)
2. Sand the outside surface of the PVC end cap flush; remove the uneven surfaces from the lettering. It is best to use a course grit (80) then a fine grit (200) sandpaper. A palm sander can be used for the initial course grit pass. It must be smooth to allow an even surface for the gaskets on the Blue Robotics sensors

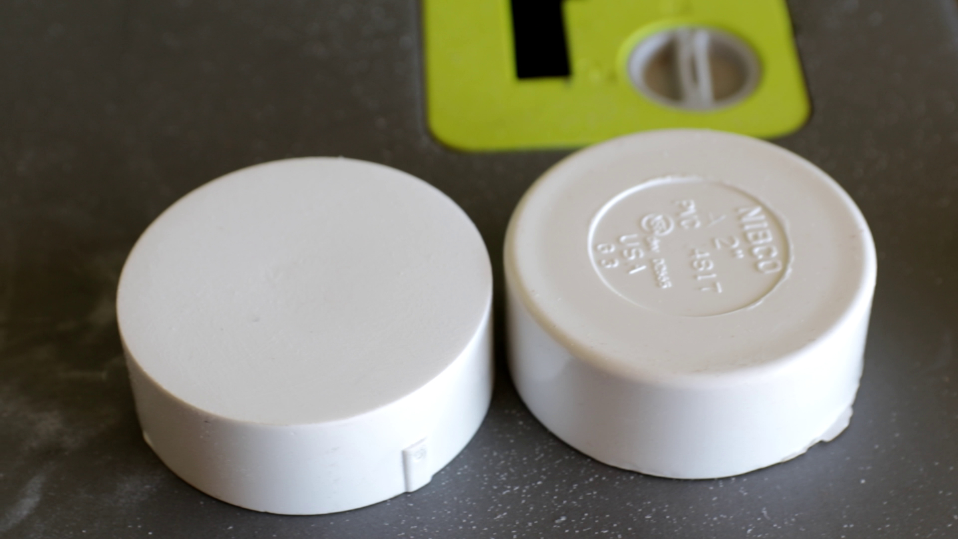
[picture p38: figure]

Figure 4.1: Smooth on the left, new on the right

15

4.1. 1.5in or 2.0in PVC | 16
3. Superglue the inside washer into the PVC end cap. This is to give the Blue Robotics sensors an even plane to screw onto. It should snap into place, so do not fully push it in until you have added the glue. Place it smooth side (3D printer bed) side up.

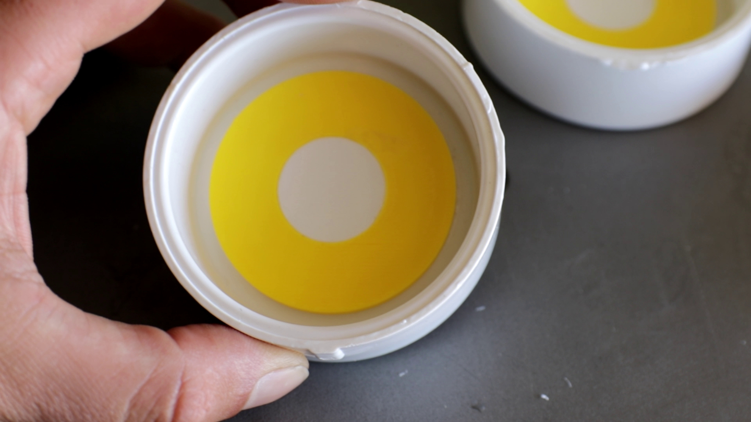
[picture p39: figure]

Figure 4.2: The washer should snap into place so do not push it all the way in until you place the Superglue under it

4. Place the drill guide inside the PVC end cap and clamp in a vice, if drilling by hand, or use drill press with a vice. Clamping the end cap in a vice should squeeze the drill guide into place so it doesn’t shift as you drill. Even if it moves, ignore it as it jumps around and maybe breaks. Do not let it get caught on your fingers/hands if it flies upward while you drill downward. So long as it helped you drill in the right place, it has served it’s purpose. This is also why you print more than one
5. Drill the holes. Start with any of them. Two 9.5 mm and one 12 mm. If the Atlas Sci probe doesn’t go in the hole, ream it out just a little bit with the drill by hand. Only a little bit, then test fit. Repeat as necessary.

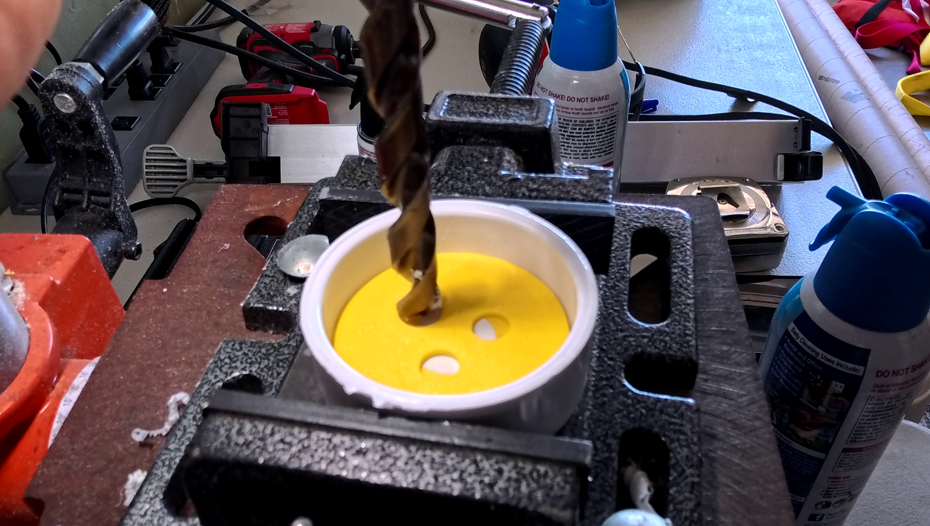
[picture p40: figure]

Figure 4.3: The end cap in the vice of a drill press. Even if/when the drill guide moves, it can break and the drill/end cap orientation does not change

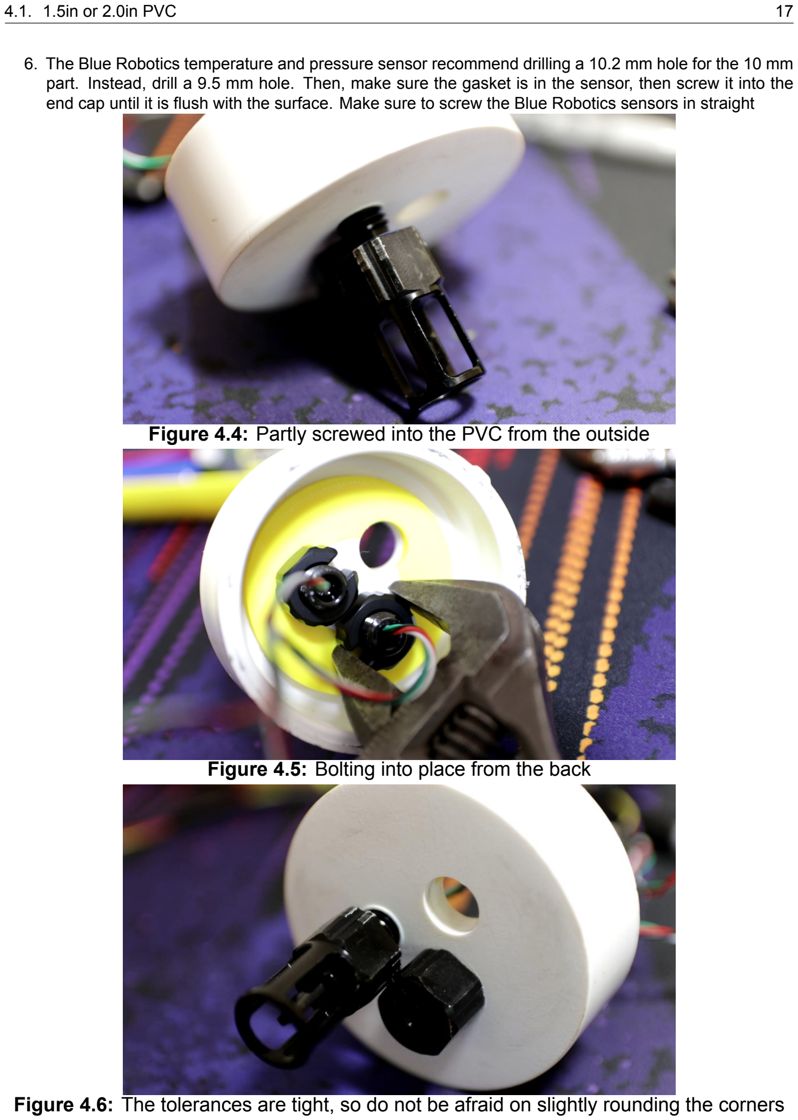
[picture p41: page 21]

4.1. 1.5in or 2.0in PVC | 17
6. The Blue Robotics temperature and pressure sensor recommend drilling a 10.2 mm hole for the 10 mm part. Instead, drill a 9.5 mm hole. Then, make sure the gasket is in the sensor, then screw it into the end cap until it is flush with the surface. Make sure to screw the Blue Robotics sensors in straight

Figure 4.4: Partly screwed into the PVC from the outside

Figure 4.5: Bolting into place from the back

Figure 4.6: The tolerances are tight, so do not be afraid on slightly rounding the corners

4.1. 1.5in or 2.0in PVC | 18
7. Sand the part of the Atlas Sci probe that will get epoxied. Slide it into place where it will go and see how much to sand. Do not sand it only in one direction – all angles make a better rough surface finish

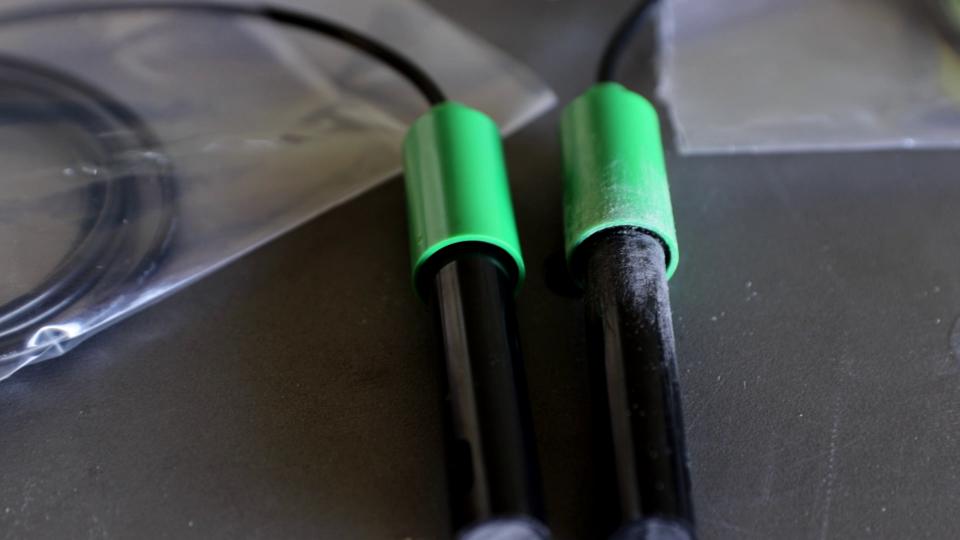
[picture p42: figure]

Figure 4.7: Smooth on the left, sanded on right

8. Situate the end cap with the now three installed sensors onto something that will keep it upright, sensor side down. A short section of 2 in PVC pipe works. Slide the epoxy ring into place to provide a dam to prevent the wet epoxy from falling off the inside raised circle into the slot where the PVC pipe will go. Resting is okay – no need to glue into place
9. Mix a 1/2 tablespoon of epoxy and stir well with a small stick/tongue depressor/similar. Carefully let gravity drop it off into the epoxy ring around all the sensor parts.
10. Gently raise and lower and spin the Atlas Sci probe to ensure epoxy gets between the probe and PVC. Use the stick to arrange the epoxy into an even surface and to make sure there are as few air bubbles as possible. If you poke the bubbles, it seems to work well
11. Place a small amount of epoxy on the end of the Blue Robotics sensor, to help provide a little strain relief where the wires come out. If they break off, it is better that they do it further from the sensor. Let dry at least six hours, or overnight

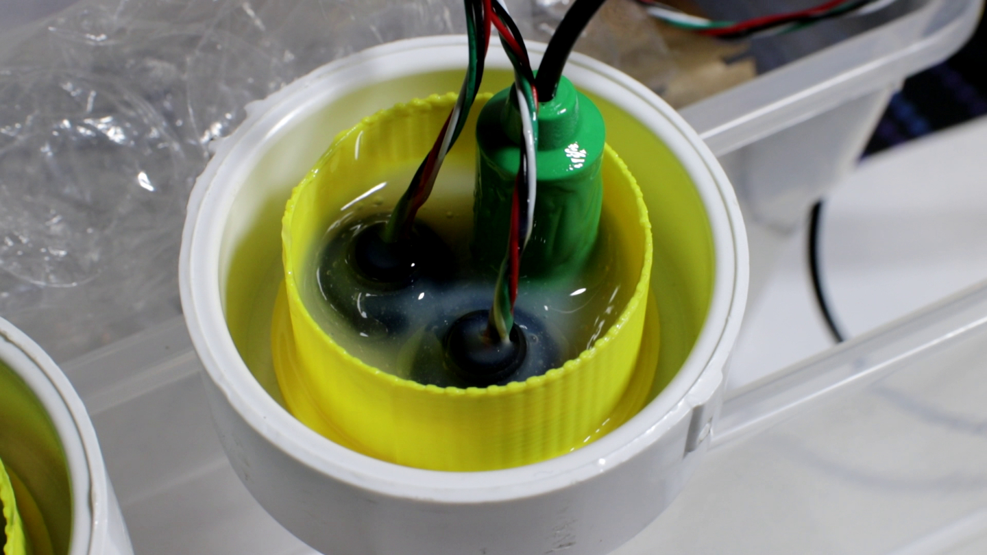
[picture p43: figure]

Figure 4.8: The ring stays in place forever now

4.1. 1.5in or 2.0in PVC | 19
12. Once dry, flip the end cap over and use Superglue to attach the protector tongs. Let that dry, then use epoxy like with the other side. Again, do your best to make no bubbles – poking them seems to work best. Fill in the area inside the protector tongs with epoxy. Let dry again for at least six hours

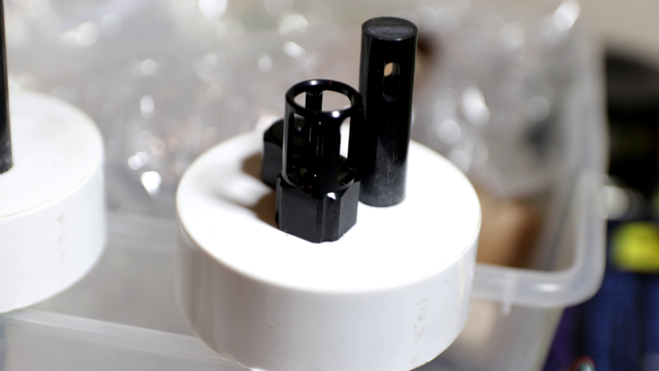
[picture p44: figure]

Figure 4.9: The top of the sensor face before epoxy. Glue the 3D printed tongs down with Superglue then put in epoxy like on the back

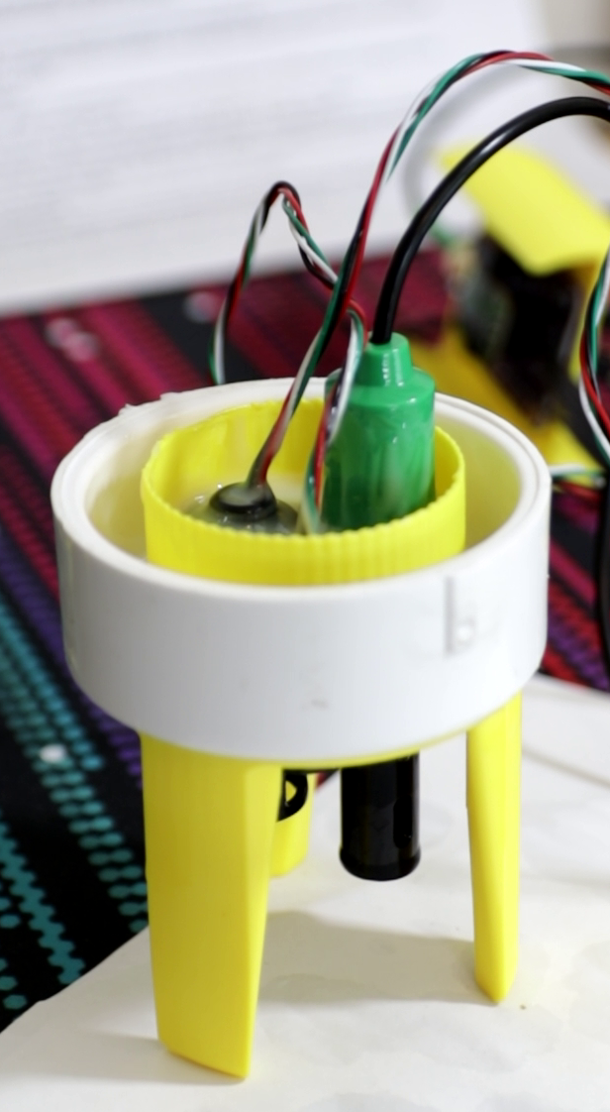
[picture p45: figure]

Figure 4.10: The end cap ready for bench testing after epoxy on both sides

### 4.1.2. System Tray

1. Glue the tray joiners to the system tray and tray extender. This is best done at the same time to ensure everything lines up. Place Superglue on the tray joiner and then hold both of them with the other two

4.1. 1.5in or 2.0in PVC | 20

parts. Kep holding it until the glue sets enough to let go
2. Glue the handle onto the flat part inside the tray extender
3. Glue the switch holder onto the handle, then put in the switch. Put the longer metal pokies on the back of the switch on the bottom side. The two short ones are for the LED in the switch, which we don’t use here for better battery endurance

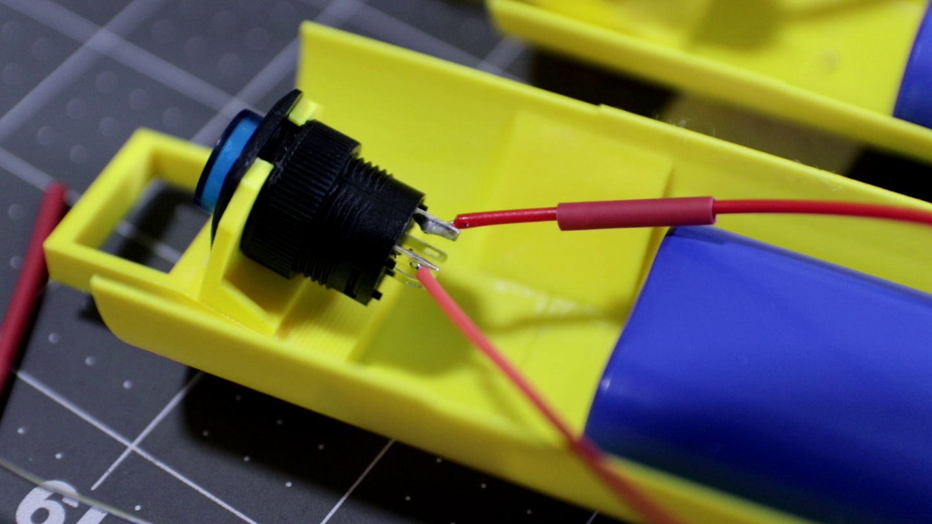
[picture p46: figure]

Figure 4.11: Here the wiring is at the top and the short connectors on the bottom are not cut; cut the short ones and solder to the long ones. The tray joiners are immediately to the left of the battery. Under the switch is the handle

4. Place the feather and RTC combo (with or without the OLED display) to get an idea of sizing for the battery. Either Superglue or Velcro tape the battery in place
5. Attach the battery’s terminal to the feather, then cut the red wire. Do not cut the black one and do not but both simultaneously or you will short the battery
6. The batteries red wire is what gets switched. Solder a longer wire to the battery’s red wire so it can reach the long metal pokie on the switch. Don’t forget to use heat shrink on both ends
7. Solder a longer wire from the now cut red battery terminal plug in the feather to the switch. Again, don’t forget the heat shrink

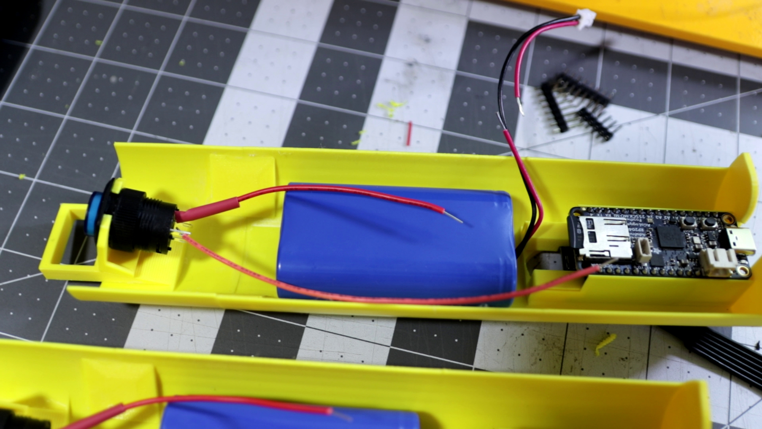
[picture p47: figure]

Figure 4.12: Note cut red wire and intact black wire from connector top right

4.1. 1.5in or 2.0in PVC | 21

### 4.1.3. Sensor Tray

The .stl file needs updating to add proper holes. This will get done by around November 2026 once Sophie is back ashore from sailing. In the meantime, drill holes in the proper locations.
1. Cut the pins off the bottom of the Atlas Scientific carrier board so the board will sit more flush on the sensor tray
2. Cut a piece or two of electrical tape to length and cover the bottom of the carrier board
3. Mark holes using the carrier board, then drill them
4. Mark holes for drilling for the Adafruit Qwiic / Stemma QT 5 Port Hub, then drill them
5. Use small bolts to attach into place

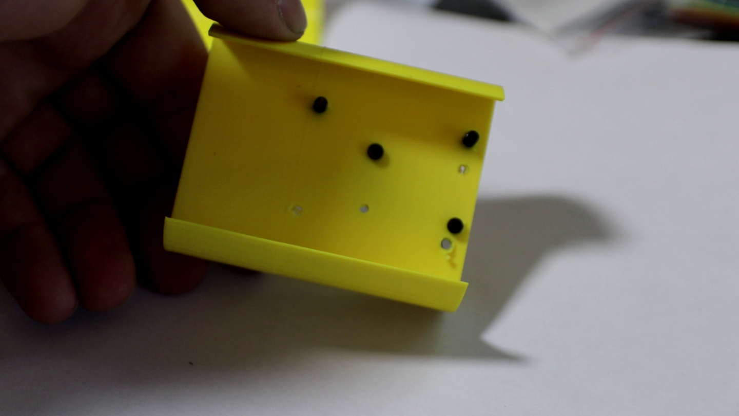
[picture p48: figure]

Figure 4.13: The back of the sensor tray after the Atlas Scientific carrier board was bolted into place, before the 5 port hub was added

Figure 4.14: The Atlas Scientific carrier board in place

At this point, you should have an end cap with three sensors epoxied into place, a system datalogger tray, and the sensor tray. Before glueing the end cap into the PVC tube, do a bench test of the system.

4.2. Temp Logger | 22

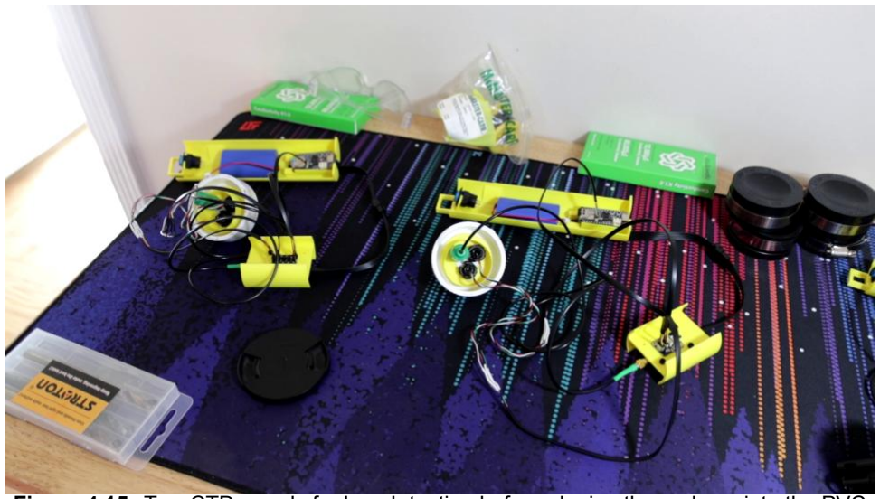
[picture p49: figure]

Figure 4.15: Two CTDs ready for bench testing before glueing the end cap into the PVC pipe

## 4.2. Temp Logger

Cost How to assemble 3D printed parts and alternatives Endurance

## 4.3. Bottom Pressure Recorder

Cost How to assemble 3D printed parts and alternatives Endurance

## 4.4. Steel Pipe

Cost How to assemble 3D printed parts and alternatives Endurance

## 4.5. Surface Float (Nalgene)

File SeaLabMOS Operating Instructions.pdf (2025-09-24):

### SeaLabMOS Operating Instructions

2025.9.24 v1
Deployment Steps
1. Unscrew the end cap. Ensure the black rubber on the end cap is clear of debris/dust
2. Inspect the inside sealing surface of the PVC and clean/wipe off debris/dust
3. Depress the white button, once
4. Observe five white flashes and one steady color for battery voltage (IAW table in box)
5. Insert end cap and tighten to finger tight. I have not used tools for the end cap safely down to (so far) 70 meters. Depending how strong your fingers are, you will reach a point where the black rubber stops expanding and the end cap spins
a. Look at the sealing surface between the black rubber and the PVC pipe. If you see something between the rubber and the PVC, remove and clean
6. Slide nose cone over pipe and electrical tape to the pipe (take photos pre/post-deployment for me please!)
7. Deploy and recover
8. Rinse with freshwater. You may feel a need to turn it off right away upon recovery, but there is plenty of time (over 24hrs+ of battery life) so there is no rush
9. Unscrew the end cap and turn off the system
a. Sometimes I’ve needed a wrench to start unscrewing the end cap. This is something I’ve experienced once the system has been at depth, but that was in Alaska with much colder water. Unsure if water temp / pressure / or both play a part. If you notice unscrewing is noticeably more difficult let me know?
Data Offload
1. Ensure the system is dry (water won’t get on the system tray when removed) and remove the end cap, placing it aside somewhere the black rubber won’t get scratched
2. Watch the sensor STEMMA QT cable, then gently slide out the system tray
a. It’ll be easier to slide in / out in a specific rotational orientation. The PVC is not perfectly circular while the 3D printed tray is. If you spin the tray inside the pipe, you will see what I mean
3. Depress the microSD card and it will click out (standard like a camera or similar)
4. Connect to computer (I’ve included a microSD card to
SD card in the box in case useful). The system is set
to UTC. It generates a new text file every power on
(example →)
a. YYYY-MM-DDThh-mm-ss.csv
5. The data will look a little weird as it has extra commas.

This is because all the SeaLabMOS use the same header. Import as usual using Python/etc using the header on the first line and it should read correctly. Remove the NANs or ignore them
6. Before the system is placed in the water you will see that brDepth has a value that is not zero (due to local atmospheric pressure). It’s on my list to do this on system power-on, but for now I account in post by zeroing the data by adding/subtracting from the brDepth column to make the depth value zero before the system got wet

Endurance (pressure only system with 2.2Ah battery)
A fully charged system (starting at 4.2V) will sample for at least 36 hours straight. It should last for around 72 hours of active sampling. I have not endurance tested a pressure only system yet but am confident to say at least 36 hours.
Charging
Plug the system into any normal USB-C phone charger. When charging, make sure to depress the power switch to connect the battery to the Feather. A solid orange LED will light up on Feather (it’s the Feather’s battery charging light that turns off when the battery is at 4.2v). If the light is blinking/flashing, it means the board has power from the USB-C but the power switch is not depressed.
The firmware does have a charge mode, but I just unplug the microSD (leaving it in the slot, just unplugged) so I don’t have to send new firmware. The onboard LED will flash red without the microSD, which is fine.
Bar30 Depth Sensor Specs (From Blue Robotics’ website)
- Relative Accuracy 0 to 60°C: ± 2 mbar (2 cm in fresh water)
- Absolute Accuracy 0 to 45°C: ±200 mbar (204 cm in fresh water)
- Resolution: 2mbar (2 mm in fresh water)
The sensor also outputs temperature, which is logged to the microSD card, but…
- Relative Accuracy | ± 2°C
- Absolute Accuracy | ± 4°C
Call/text anytime if questions or troubleshooting issues
Happy sampling!
Sophie Scopazzi

Aspect Wave LLC
707-520-4460
aspectwave@pm.me

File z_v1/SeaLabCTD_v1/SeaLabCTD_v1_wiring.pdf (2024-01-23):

G

SDA

SCL | | | | | + | -
5v | 5v | G | A5 | A4 | 5v | G
CS | 10 | R | R
DI | 11 | G
DO | 12 | R
CLK | 13 | G | R

G G

5v | 5V
| | | | 2 3
| | G
5V | VCC | G
- | PRB | TX
G | PRB | RX

LED

Power
barrel in | Switch

### Battery

I2C
convert.

Depth /
Pressure
Sensor

Arduino Uno v3 w/
Screw Terminal Block Breakout Shield Module SD

Salinity BNC
Connector

Salinity
Sensor

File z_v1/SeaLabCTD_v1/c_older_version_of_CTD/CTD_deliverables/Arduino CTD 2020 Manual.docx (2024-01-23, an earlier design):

Created by Anthony Scopazzi

Spring 2020

Contents

What is a CTD? Page 1

Why CTD’s are used

Example plots with explanation

Getting Started Page 2

Equipment and Software

Troubleshooting Arduino IDE - COM port, other problems

Intro Breadboard and Wiring

Intro Soldering

Intro Coding

Temperature Sensor Page 4

Wiring

Collecting temp calibration data

Parsing Data in Excel

Example final graphs Salinity Sensor Page 9

Explanation

Wiring

Calibrating salinity

Pressure Sensor Page 10

Explanation

Wiring and Testing

Micro SD Card Breakout Board Page 11

Explanation

Wiring

Waterproof Housing Page 12

3D printed equipment tray

Making the housing

Arduino Programs Page 13

What is a CTD?

CTD stands for Conductivity, Temperature, and Depth as that is what a CTD measures. Basically, what the instrument does is measure the salinity and temperature at a depth, which can be displayed in graphs such as ones below.

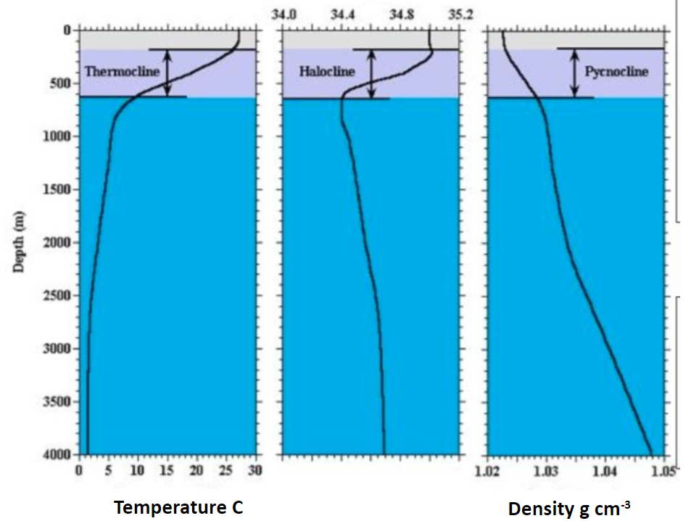
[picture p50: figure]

This instrument, which supplies what may seem like simple datapoints, can help answer a lot of questions about the water column deployed in. Using the information from a CTD it is possible to infer further and answer many questions such as: Is the water column stable and not mixing, or unstable and prone to mixing? What is the depth of the thermocline or halocline? How would that effect the life living in the epipelagic (the top photic zone)?

Helping to answer questions like that enables scientists to better understand the entire system they are studying with a relatively simple device. Usually, these instruments cost $5,000 or more, but through this manual we will build one for less than $500.

Getting Started

Board and Sensors

Arduino Uno R3 ($20)

Dallas Temp Sensor DS18B20 Temperature Sensor (~$10 each = $30 total)

Atlas Scientific EZO-EC Embedded Conductivity Circuit ($240 for Conductivity K Kit)

SparkFun Pressure Sensor Breakout - MS5803-14BA ($60)

Total Cost = $350 plus cost of wires, etc.

Misc Equipment

Soldering iron and accoutrement

Heatshrink

Solid core wires

Wire strippers / cutters
Safety glasses

Software

Arduino IDE software - only works on PC

https://www.arduino.cc/en/main/software

Unable to connect to board - COM PORT error

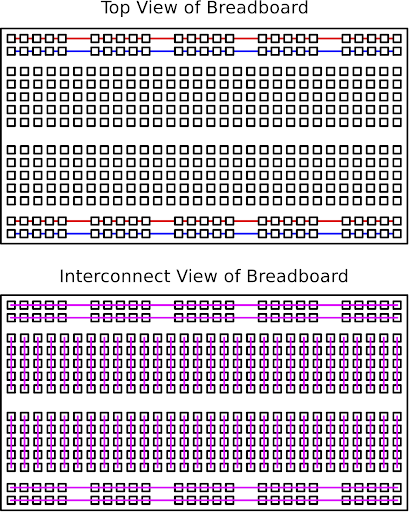
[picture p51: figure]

1 - make sure USB is plugged into computer

2 - Navigate to ‘Tools’ --> ‘Port’ --> select ‘Arduino UNO’

3 - Try a different cable, restarting the program/computer, unplug/replug

4 - Ask teacher

Intro Breadboards

Breadboards are for temporary testing of wiring and are connected as shown right. The holes down the sides with red and blue colors go all the way down the board, to be used as hot (red) and ground (blue). The inside is connected as shown and is where components go. Common errors are not putting the wires into the row with a component and mixing up hot and ground connections. Being consistent with colors is also incredibly helpful.

Intro Soldering

Safety – Always wear safety glasses when soldering! Small pieces of flux or solder can fly off and get in your eyes. Just wear them – it’s not worth the potential for eye problems. Try not to breath in the solder smoke. It’s the flux on the solder burning. It won’t kill you but is not good for you either. Just don’t breathe it the best you can.

General – Given the choice (and you have a choice) but consistent with wire colors. Future you will thank past you. Red = hot, power, voltage | Black (or blue if don’t have black) = ground

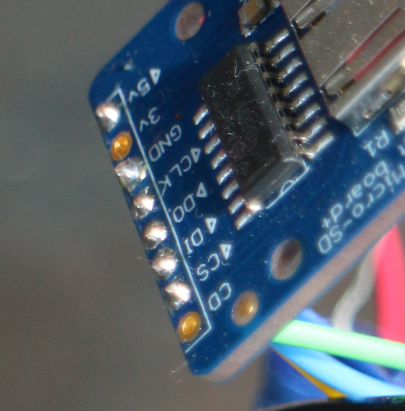
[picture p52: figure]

Stripping and Soldering – Use wire strippers of the correct size and expose only about 5mm of wire and before attaching the wires slip on some heat shrink. Put into the board and solder. It should look something like the photo on the right. Clip the extra wire and inspect to be sure you did not bridge any connections. If you did unsolder and redo.

Intro Coding

Common errors

Not having a “;” at the end of lines

Baud rate in code different than in serial monitor

Missing a capital letter, or having one where there shouldn’t be

Helpful commands

//To leave a line in, but not have it be ran code, comment out the line with two “//” before it

#define rx 2 //define what pin rx is going to be, “tx” would be transmit

Serial.begin(9600); //sets baud rate for the hardware serial

//leave concise notes in your code, ideally in the same line, to make sure you can go back and know what it’s doing. Do it in the same line to keep it readable.

Use the code in the appendix or downloaded zip file for individual sensors and final code

Dallas Temp Sensor (DS18B20 Temperature Sensor)

https://lastminuteengineers.com/ds18b20-arduino-tutorial/

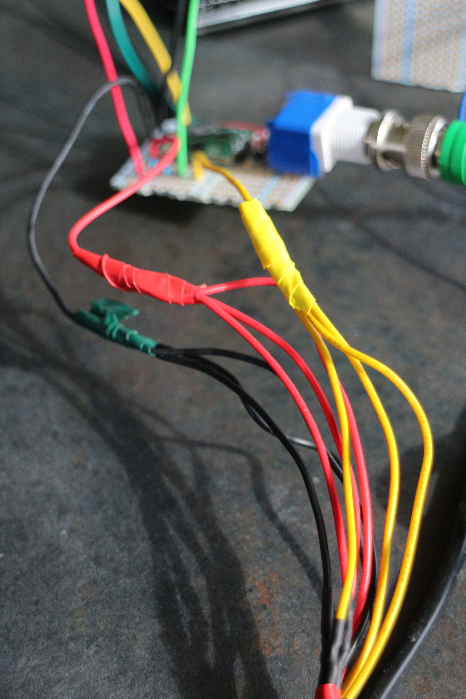
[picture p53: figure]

Explanation

While these are cheap, they do work well, especially with three averaged together. By using three in this manner we can get a very accurate picture of the real temperature – the downside being they do not have the fastest response rate. This is compensated for by lowering slowly into the water when deploying.

Getting Sensor Ready to Wire

Three individual sensors for an array – each has three wires. Strip and solder each wire from the sensor to a solid core wire.

As you have three sensors and one pin on the Uno you must connect the matching colors of each sensor into one wire that gets plugged into the board, as shown to the right. Be sure to color each wire consistently and to heat shrink the exposed wire. If you don’t have heat shrink big enough use electrical tape as in the photo (heat shrink is preferable.

Wiring Temp Sensors

Be sure to use a 5k ohm resistor (4.7k-5.2k)

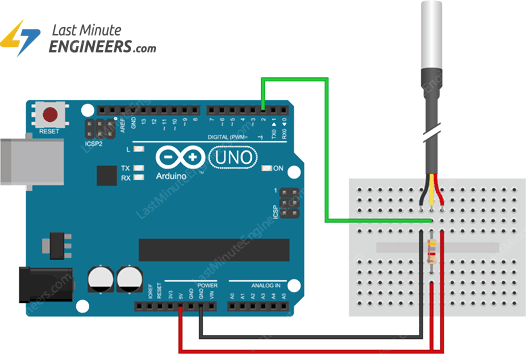
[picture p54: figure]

Testing Temp Sensors

Wire them as in the diagram above, then use the code “tempSensor_test.ino” to make sure they work. Troubleshoot with each other, or the teacher, if they do not work/display correctly. One sensor might display -127 as its reading; this mostly likely means there is a problem with one of your wired connections. One of the sensors may have a wire soldered poorly or it may not be fully connected in the breadboard. Once everything’s working, start calibrating!

Collecting Temp Calibration Data

The idea is to heat all the sensors at the same heat and see how they react in comparison to each other. Gather the following materials:

Arduino and sensors Bunsen burner with stand

Yellow temp sensor Beaker to fill with water

1) In the room temperature tap water (about 20C) place the three sensors so they do not touch the bottom of the glass. Do the same with the yellow temp sensor.
2) Once you turn on the bunsen burner, clear the serial monitor and record a reading of the yellow every 10 seconds until the water reaches about 90C. It should take at least a few minutes.
3) As soon as the water reached about 90C unplug the Arduino from the computer. This will stop the serial monitor from moving so you can copy all the information to Excel.
4) Put the yellow temperature sensor data at the appropriate ten second intervals in your data.

Parsing Temp Calibration Data in Excel

Copy and paste the data into an Excel column. It should look something like this:

25.25,26.44,26.75
25.5,26.44,27
25.81,26.5,27.25

Select the above column, then go to “Data” and select “Text to Columns”

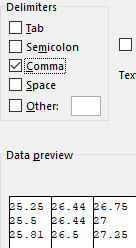
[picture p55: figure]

Make sure “Delimited” is selected. It should be by default. Click Next.

Deselect Tab and check Comma. The data below should look like this image.

Click Next then Finish

The data should look like this table in Excel. Go about graphing!

25.25 | 26.44 | 26.75
25.5 | 26.44 | 27
25.81 | 26.5 | 27.25

Final Temp Calibration Graphs

Using a standard error of +- one you can see the average of the three sensors is within the acceptable margin of “reality” from the yellow temperature sensors. The time is in minutes and seconds. As you will see in the next graph, the individual sensors are not exactly on the average, but together they match reality well.

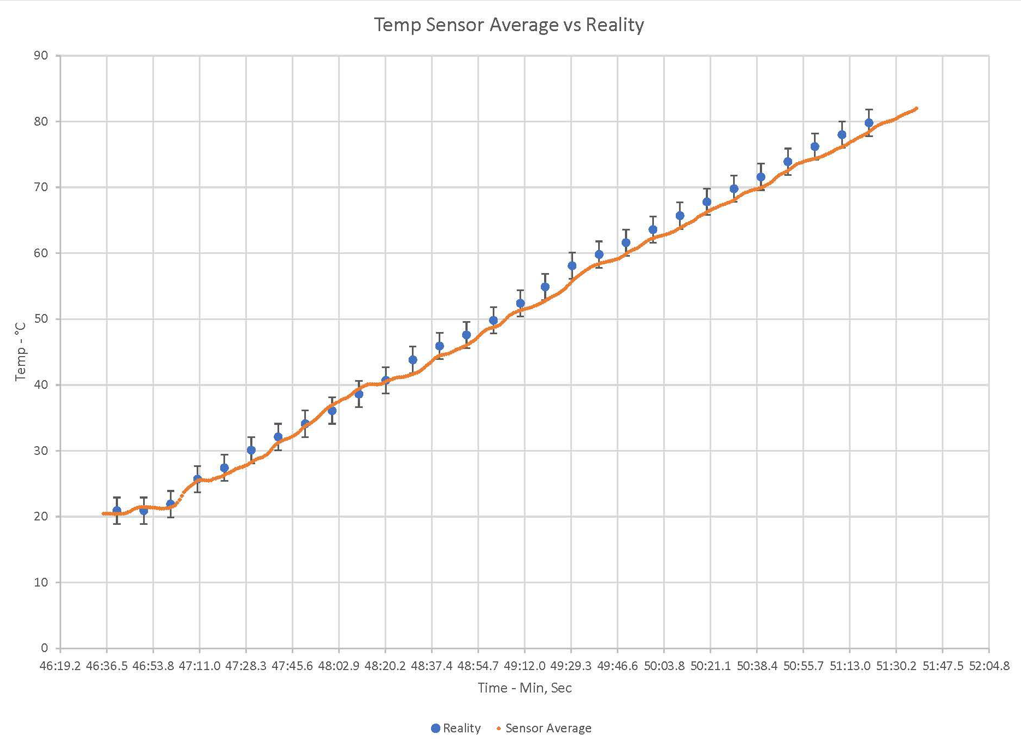
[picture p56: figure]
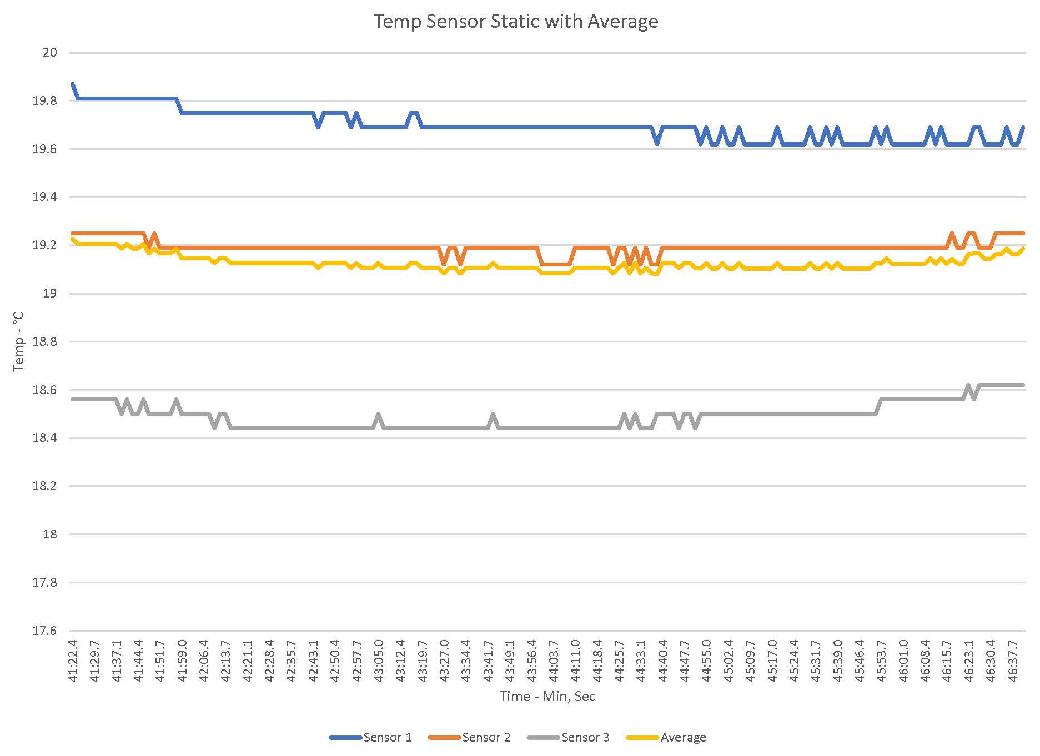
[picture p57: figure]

The variance in a static temperature of the sensors over 5 minutes. There is about a one degree variance between the gray and blue, but on average they are accurate to the real temperature.

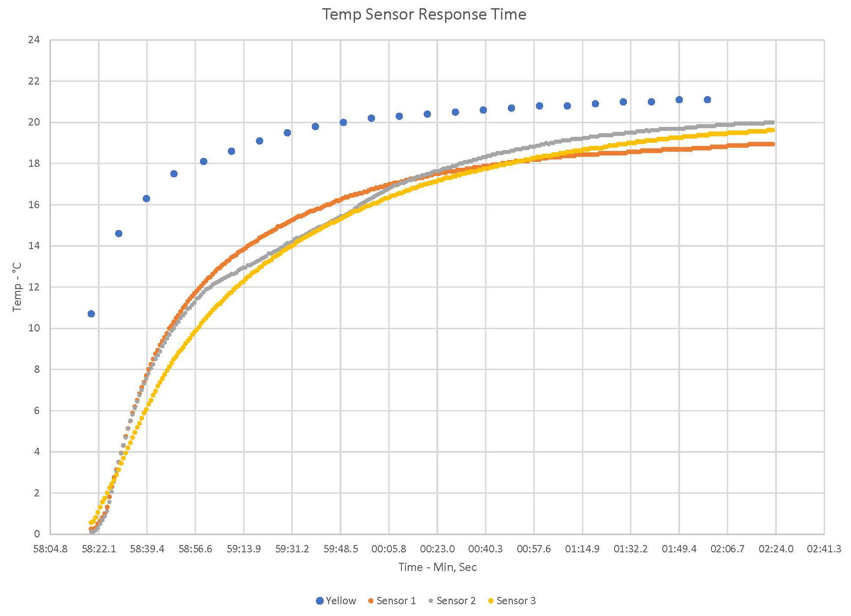
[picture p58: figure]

The response time of the sensor when taken out of ice water to come to room temperature. This isn’t as important to know as if they are accurate, as in the first graph, but it is a good data point to know if only to realize that you can’t move the CTD too fast through the water column if you want accurate data. They took about two minutes in air to come to come to ambient temperature. They’d be faster in water, as it conducts heat better, just don’t rush.

Atlas Scientific EZO-EC Embedded Conductivity Circuit

https://www.atlas-scientific.com/product_pages/kits/ec_k0_1_kit.html

Explanation

This sensor can tell you the TDS (Total Dissolved Solids), EC (Electrical Conductivity) and supposedly tell you the SAL (Salinity). However, in our case we only care about getting the EC data from the device as we will calculate the salinity based on that information ourselves.

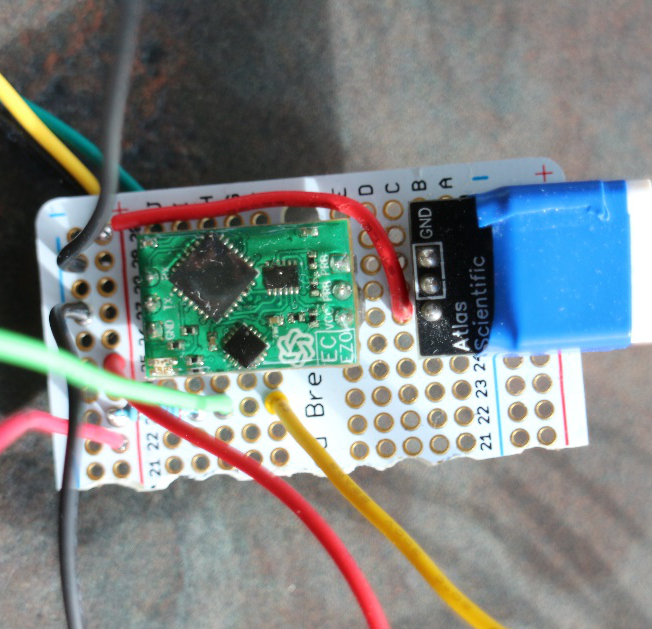
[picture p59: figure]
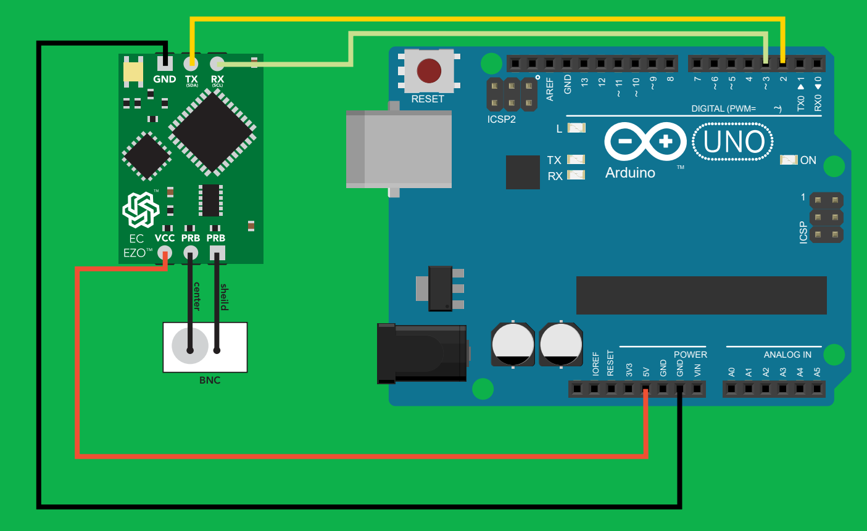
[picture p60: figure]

Wiring Salinity Sensors

There is an important part of the wiring missing from the diagram, that is explained in the datasheet for the sensor. Both parts of the equipment need 5V power, not just the part in the green diagram. Connect it the same way as shown on right, but in a breadboard, so both pieces get 5V of power. The red bent wire close to the board is supplying power from the hot on the left to the row both of their power is in. It might not be clear right away which pin is the center and shield, so lay it out as in the photo. It’s also recommended, once you get to the soldering stage, to electrical tape around the sensor as shown (blue tape on right) to avoid any shorts.. Bench test in and once everything’s working, start calibrating!

Calibrating Salinity

Using the code “salinSensor_test.ino”, follow the instructions found in the EZO-EC Conductivity Circuit Datasheet in order to calibrate the sensor using the correct liquids. Once you have calibrated your sensor be sure to label the sensor and components, so you always use the same sensor and board.

MS5803-14BA Pressure Sensor Breakout Board

https://learn.sparkfun.com/tutorials/ms5803-14ba-pressure-sensor-hookup-guide

Explanation

This sensor is used to tell depth, as pressure is a highly accurate way to tell the depth in a water column. Without this sensor the rest of the data would be worthless, as without depth to compare it to it is impossible to create the graphs needed to analyze the water column.

Wiring Pressure Sensor

This diagram is also missing a key component to make it function correctly. As stated in the manual (that’s why you look at the manual) a 100-microfarad capacitor must be placed in series with the 3.3V power supply to the board as seen below. Without this the sensor will display a semi accurate a reading; however, the reading will vary more. Use code “pressSensor_test.ino”

The cylinder is a 100-microfarad capacitor in series (soldered) to the power wire connected to the power on the Uno

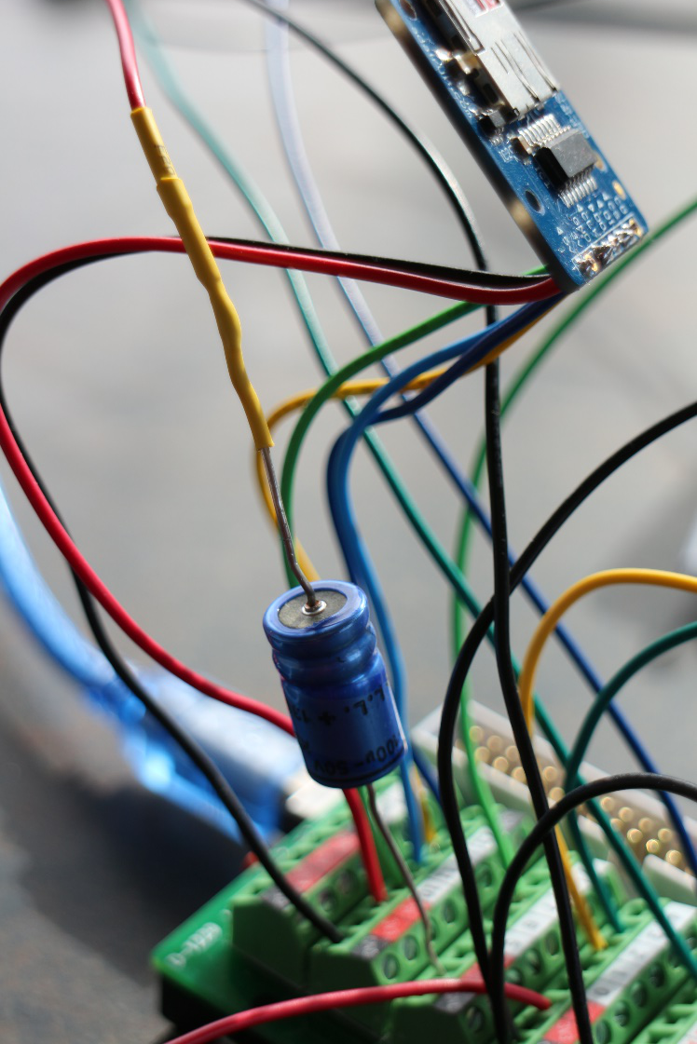
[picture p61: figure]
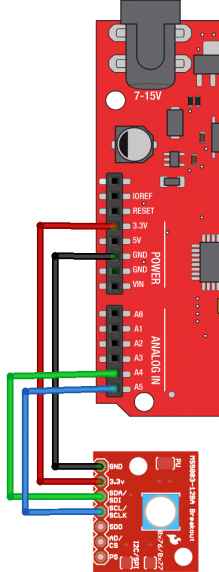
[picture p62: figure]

Micro SD Card Breakout Board

https://www.adafruit.com/product/254

Explanation

As the whole sensor package will be going underwater there must be a way for the Uno to save the sensor data locally – a microSD card. The wiring is relatively simple, but the coding is more difficult.

Wiring SD Card

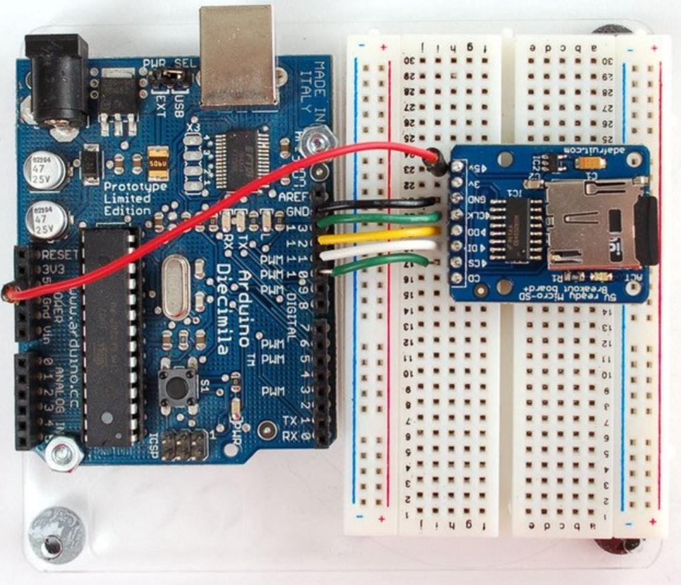
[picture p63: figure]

Waterproof Housing

While PVC is cheap and relatively easy to waterproof, 2” PVC is only rated for 280PSI. That means it’s only good to a depth of 91’. This is relatively shallow but might be good enough for your situation. Ideally, an aluminum housing would be ideal. One side with sensors, one side you can screw with a gasket.

3D printed equipment tray

It’s recommended, but not necessary, to 3D print a tray to slide in and out of the housing, to make working on the equipment easier. This also has the bonus of securing the equipment more securely, so it jostles less as you deploy it. See zip file for printer STL file.

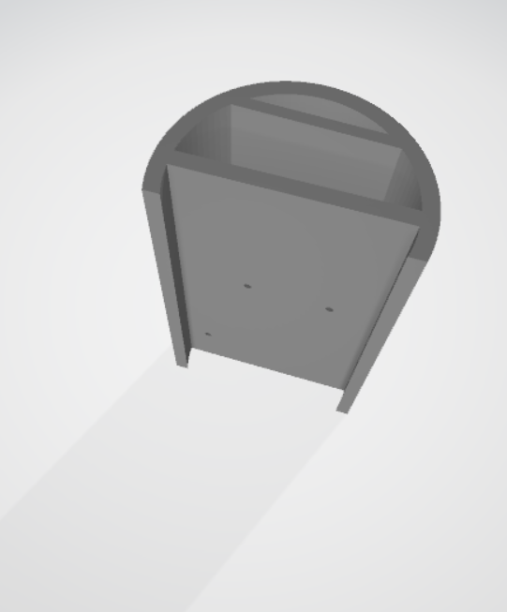
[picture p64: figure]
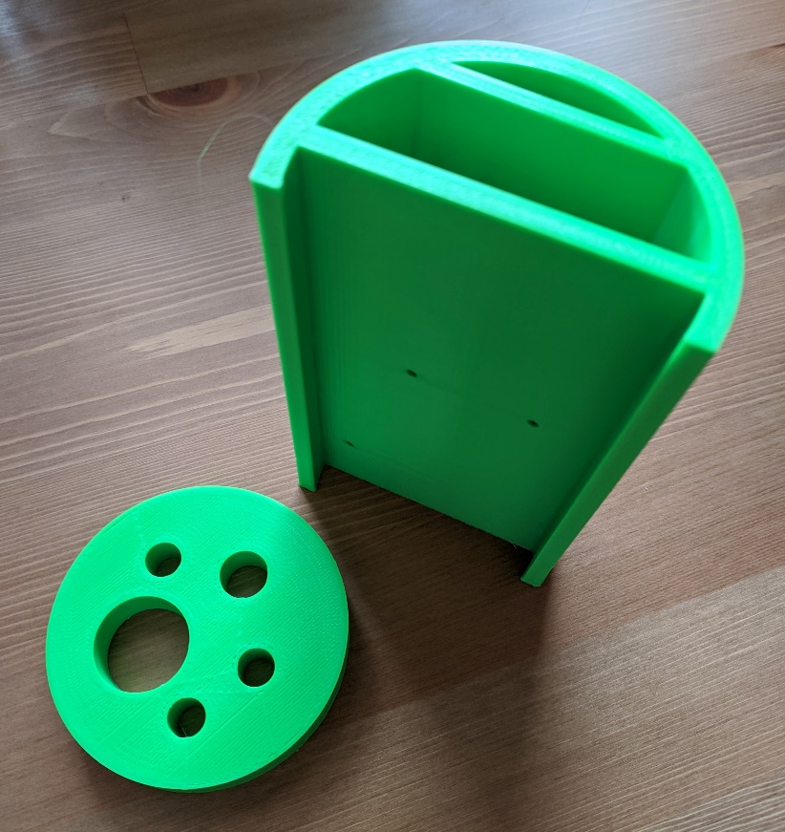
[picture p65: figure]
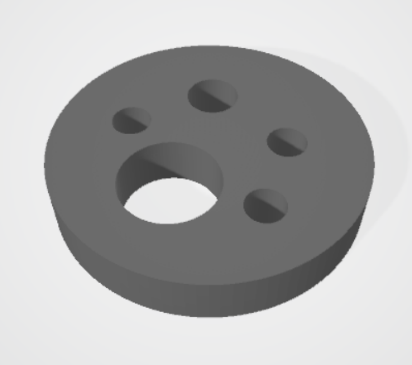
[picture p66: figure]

Making the housing

Using 3” PVC pipe make an approximately 1.5’ section. On one end you shall have to secure the 3D printed sensor array or using a PVC end cap drill holes the correct size for the sensors. Either way it’s done, permanently secure and watertight the connection of the sensors through and it to the pipe. This end stays permanently attached. The other end is what you will open to slide the tray in and out in order to access the Arduino. A 3" PVC cleanout plug could be used as the screw able end cap.

Arduino Programs

See README in the zip file for explanation of what the files are.

Takeaways and Final Thoughts

Although I was not able to finish the project – i.e., put in a housing and put in the water – I was able to get all the equipment ready to put in a housing. I would not have been able to do this without the help of my best friend ‘Vizi’, as he is wholly responsible for the final program that creates the text files and the README file. Together we went through almost 200 revisions to the deployment code; quite simply, without him the code would not have happened.

There are a few takeaways I would mention to students attempting this in the future:

- Take detailed notes every step of the way. A week later when you return to the project you can know exactly where you left off. It also greatly helps in the coalition of documents such as these.
- Take the time to understand how the breadboard works and stay consistent with the colors of your wires. You do not want to wire everything together, have it not work, and have to start from scratch if you can’t find the one wire that’s in the wrong spot. Knowing the breadboard and being consistent makes finding the one awry wire much easier.
- Do not sit and wallow in a ‘stuck’ state. If you are stuck on something ask your teacher, fellow students, and do not give up! The answer is out there – it is not impossible. More than once I got frustrated with something not working so I would move on and try again the next day. Sleeping on it and coming back tomorrow can be helpful.

Arduino CTD 2020 Manual

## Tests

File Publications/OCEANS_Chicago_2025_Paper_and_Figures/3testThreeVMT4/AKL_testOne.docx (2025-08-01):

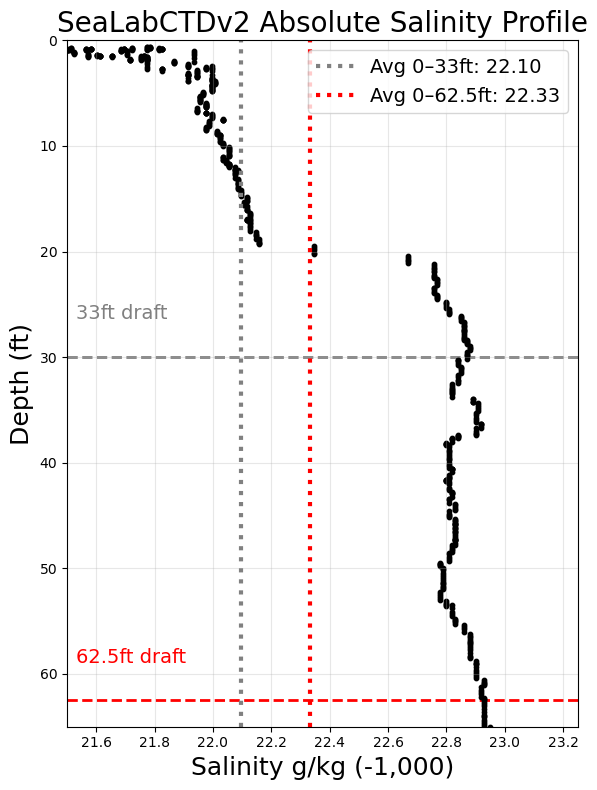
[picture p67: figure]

Test Date and Time: 29 APR 2025, 1439 – 1443 (ZD+8)

Avg Sampling Frequency: 4.97 Hz

Location: Valdez Marine Terminal Berth 4

CTD Cast Location on Vessel: while vessel portside to, CTD cast from the starboard side on the maindeck astern of the liferafts

Tide: +5.2ft

Average salinity 0-33ft: 1022.10

Average salinity 0-62.5ft: 1022.33

Difference: 0.23

Surface salinity: 1021.50

Salinity at 62.5ft: 1022.93

Difference: 1.43

Qualitative Assessment of Weather: Raining before the cast for a ~6 hours – light to medium rain, 0.1” an hour. Very light drizzle at time of cast.

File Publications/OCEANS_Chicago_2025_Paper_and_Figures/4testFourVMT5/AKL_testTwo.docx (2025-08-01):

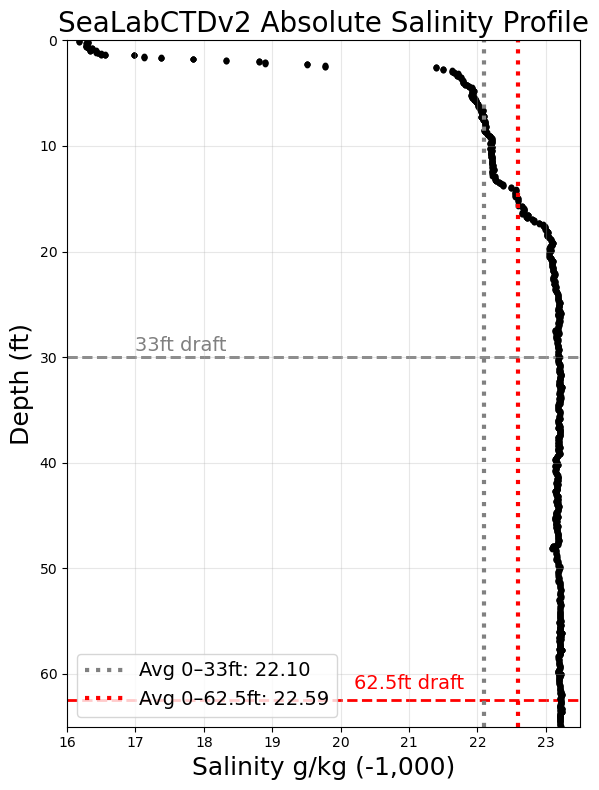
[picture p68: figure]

Test Date and Time

10 MAY 2025, 1554 – 1606 (ZD+8)

Avg Sampling Frequency

4.98 Hz

Location

Valdez Marine Terminal Berth 4

CTD Cast Location on Vessel

Ship starboard side to berth. CTD cast from port side on maindeck astern of the FRB

Tide: +6.5ft

Average salinity 0-33ft: 1022.10

Average salinity 0-62.5ft: 1022.59

Difference: 0.49

Surface salinity: 1016.1

Salinity at 62.5ft: 1023.1

Difference: 7.0

Qualitative Assessment of Weather

Sunny and clear

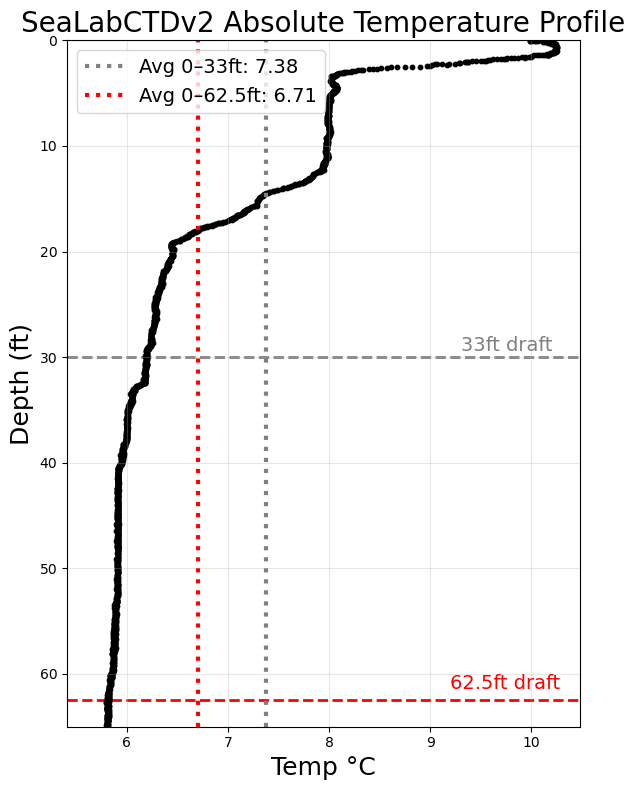
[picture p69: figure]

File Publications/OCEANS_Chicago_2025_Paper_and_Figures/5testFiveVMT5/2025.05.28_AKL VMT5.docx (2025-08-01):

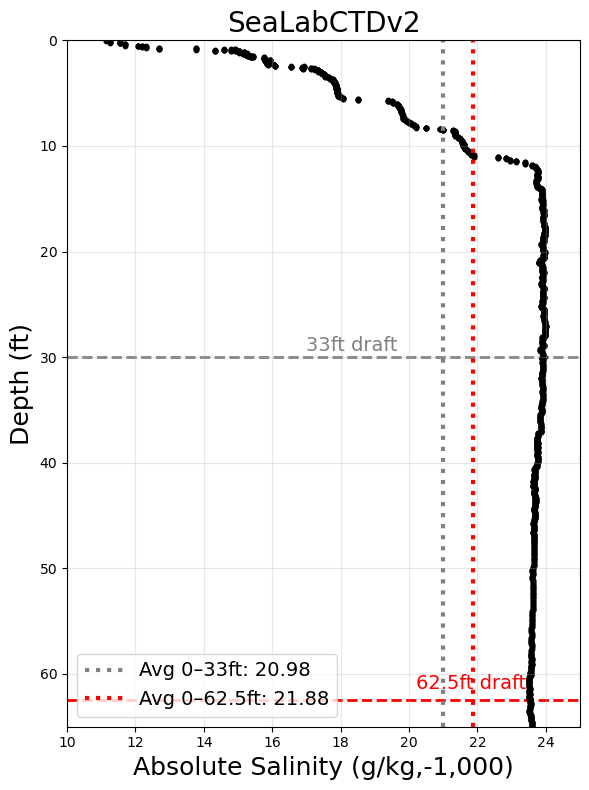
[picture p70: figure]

Test Date and Time

28 MAY 2025, 1214 – 1225 (ZD+8)

Avg Sampling Frequency

4.98 Hz

Location

Valdez Marine Terminal Berth 5

CTD Cast Location on Vessel

Ship starboard side to berth. CTD cast from port side on maindeck astern of the FRB

Tide: +6.5ft

Average salinity 0-33ft: 1021.0

Average salinity 0-62.5ft: 1021.9

Difference: 0.9

Surface salinity: 1011.1

Salinity at 62.5ft: 1023.9

Difference: 12.8

Qualitative Assessment of Weather

Cloudy and clear, no rain

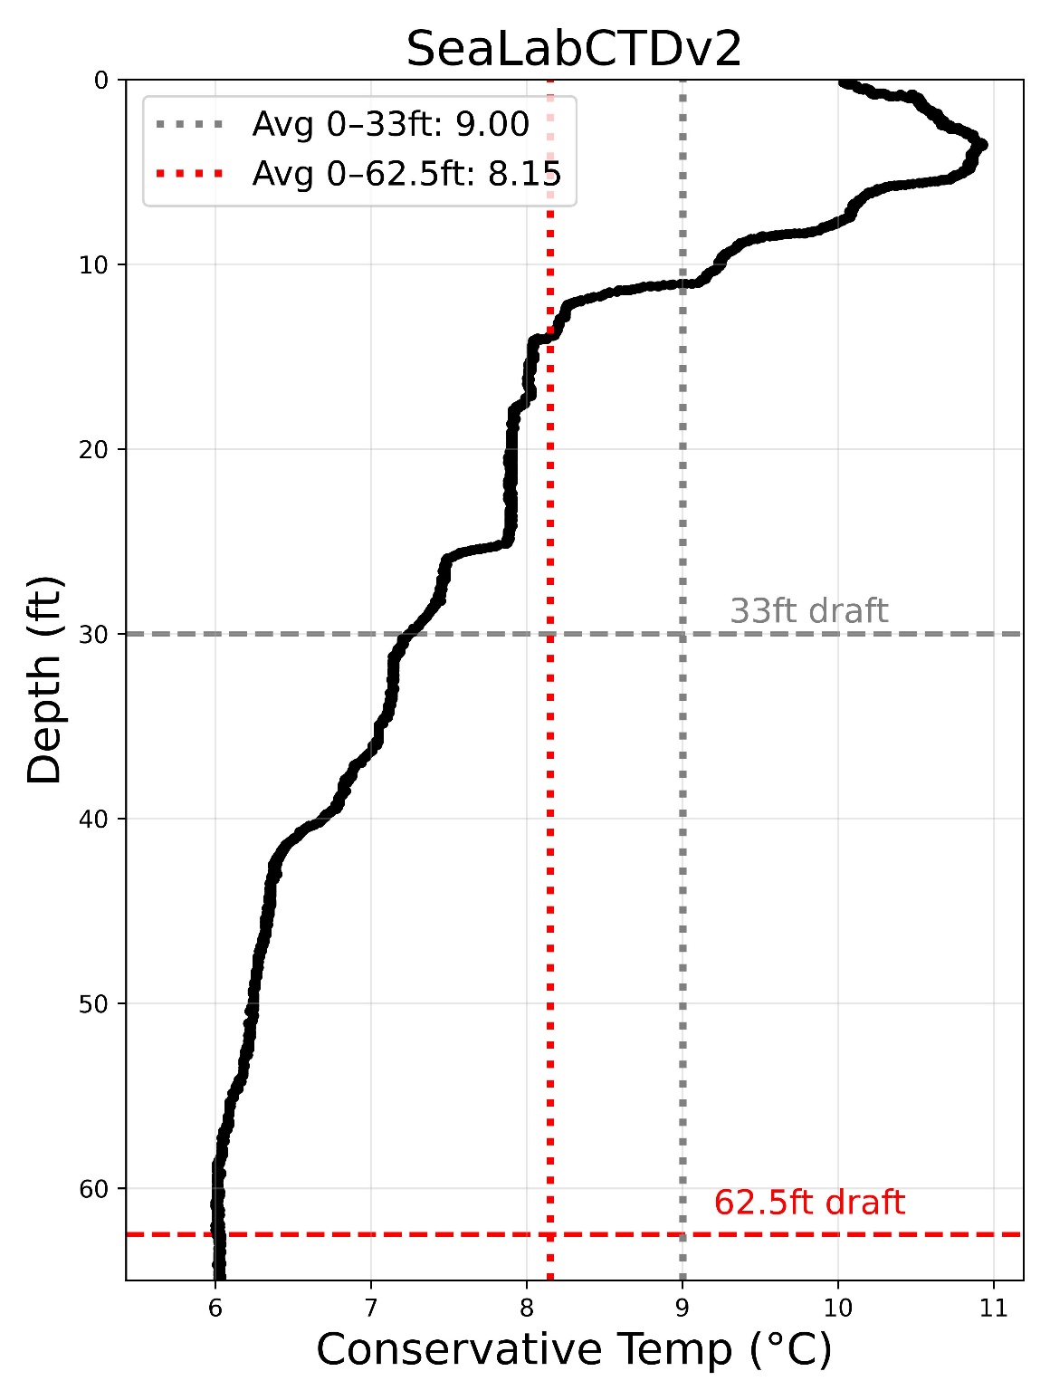
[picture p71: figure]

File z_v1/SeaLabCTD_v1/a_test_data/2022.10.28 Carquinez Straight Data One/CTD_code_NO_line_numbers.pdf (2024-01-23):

% _ | _ | _ | _____ _______ _____
% | | | | | | | | / ____|__ | __| __ \
% | |__| | ___ _ __ ___ | ___| |__ _ __ _____ | __ | | | | | | | | |
% | __ |/ _ \| '_ ` _ \ / _ \ '_ \| '__/ _ \ \ /\ / / | | | | | | | | |
% | | | | (_) | | | | | | __/ |_) | | | __/\ V V / | |____ | | | | |__| |
% |_| |_|\___/|_| |_| |_|\___|_.__/|_| \___| \_/\_/ | \_____| |_| |_____/
% (ASCII font Big from https://www.coolgenerator.com/ascii-text-generator

% Homebrew CTD Data Grapher / Visualizer
% Author: Sophie Scopazzi
% Author Website: sophiescopazzi.com
% Date: OCT 2022

% always
clear all
close all

%% INSTRUCTIONS - HOW TO USE THIS CODE
% There are comments throughout code as well
% If you want to contact me about this code, use my website

% 1. Put this script in same folder as datafile.txt
% Check name of datafile is the same as in the script
% 2. Ensure sensors are in the correct order in the data from the Arduino % script, or none of it will make sense (EC, TDS, sal, etc) in order % 3. Fine correct time values in this plot, record for next step
% Want data from downward travel, upward water column is disturbed % 4. Recomment step 3, put the values recorded into DEPLOY DATA PULLING % 5. Plots or subplots as desired. Set xlims and ylims as necessary

%% 2. DATA INGEST AND CLEANING
% datafile from CTD, ensure name is correct, script in same folder as data data = readtable('DATAFILE.TXT');

% ensure the data is labeled correctly, will depend on Arduino code
% get data from data table, BUT it has nans
EC_nans | = | data(:,1); %EC data
TDS_nans | = | data(:,2); %TDS
sal_nans | = | data(:,3); %salinity
mbar_nans | = | data(:,4); %mbar
temp_nans | = | data(:,5); %temp in C
dmeter_nans | = | data(:,6); %depth in meters

% take nans out of above data
EC_table | = | rmmissing(EC_nans);
TDS_table | = | rmmissing(TDS_nans);
sal_table | = | rmmissing(sal_nans);
mbar_table | = | rmmissing(mbar_nans);
temp_table | = | rmmissing(temp_nans);
dmeter_table = | rmmissing(dmeter_nans);

% convert data from table to array for plotting / manipulation
EC | = | table2array(EC_table);
TDS | = | table2array(TDS_table);

sal | = | table2array(sal_table);
mbar | = | table2array(mbar_table);
temp | = | table2array(temp_table);
dmeter | = | table2array(dmeter_table);

% convert mbar to feet, incase you want to do that
% depth_feet = mbar.*0.033455256555148;

% convert meters to feet, in case you want to use the Mapping Toolbox
% deploy_feet = distdim(dmeter,'meters','feet'); %(needs Mapping Toolbox) dfeet = dmeter.*3.28084; % I didn't want to use Mapping Toolbox

%% 3. TO FIND CORRECT START / STOP VALUES IN TIME
% FIND TIME VALUES IN THIS PLOT
% look in this plot to find where depth values start and stop % this is what you will put in below, the (93:135), etc
% uncomment below --- 56-59
% n = length(mbar);
% time = 1:n;
% figure;
% plot(time,mbar);

%% 4. DEPLOY DATA PULLING
% take out only parts of the data for deployments % this is the values found 'FIND DEPTH VALUE PLOT' % if you have more or less than four, change it

% ONE
deploy1_EC | = | EC | (93:135,1);
deploy1_TDS | = | TDS | (93:135,1);
deploy1_feet | = | dfeet | (93:135,1);
deploy1_temp | = | temp | (93:135,1);
deploy1_sal | = | sal | (93:135,1);

% TWO
deploy2_EC | = | EC | (609:660,1);
deploy2_TDS | = | TDS | (609:660,1);
deploy2_feet | = | dfeet | (609:660,1);
deploy2_temp | = | temp | (609:660,1);
deploy2_sal | = | sal | (609:660,1);

% THREE
deploy3_EC | = | EC | (774:799,1);
deploy3_TDS | = | TDS | (774:799,1);
deploy3_feet | = | dfeet | (774:799,1);
deploy3_temp | = | temp | (774:799,1);
deploy3_sal | = | sal | (774:799,1);

% FOUR
deploy4_EC | = | EC | (832:979,1);
deploy4_TDS | = | TDS | (832:979,1);
deploy4_feet | = | dfeet | (832:979,1);
deploy4_temp | = | temp | (832:979,1);
deploy4_sal | = | sal | (832:979,1);

%% 5. GRAPHS
% however many you did, make that many subplot graphs
% or you can put them on their own plots (not subplot them)
% these are the same with the numbers changed, 1-4
figure;
subplot(2,2,1); % subplot since I want four graphs on one figure plot(deploy1_temp,deploy1_feet,'red');
title('One');
hold
plot(deploy1_sal,deploy1_feet,'blue'); set(gca,'Ydir','reverse'); % to make zero the top of Y axis ylim([0 40]); % use the depth you deployed
xlim([14.5 19]) % use the range of your data legend('temp','salinity')
ylabel('depth (ft)');
xlabel('°C | PSU (ppt)');

subplot(2,2,2);
plot(deploy2_temp,deploy2_feet,'red'); title('Two');
hold
plot(deploy2_sal,deploy2_feet,'blue'); set(gca,'Ydir','reverse');
ylim([0 40]); % use the depth you deployed xlim([14.5 19]) % use the range of your data legend('temp','salinity')
ylabel('depth (ft)');
xlabel('°C | PSU (ppt)');

subplot(2,2,3);
plot(deploy3_temp,deploy3_feet,'red'); title('Three');
hold
plot(deploy3_sal,deploy3_feet,'blue'); set(gca,'Ydir','reverse');
ylim([0 40]); % use the depth you deployed xlim([14.5 19]) % use the range of your data legend('temp','salinity')
ylabel('depth (ft)');
xlabel('°C | PSU (ppt)');

subplot(2,2,4);
plot(deploy4_temp,deploy4_feet,'red'); title('Four');
hold
plot(deploy4_sal,deploy4_feet,'blue'); set(gca,'Ydir','reverse');
ylim([0 40]); % use the depth you deployed xlim([14.5 19]) % use the range of your data legend('temp','salinity')
ylabel('depth (ft)');
xlabel('°C | PSU (ppt)');

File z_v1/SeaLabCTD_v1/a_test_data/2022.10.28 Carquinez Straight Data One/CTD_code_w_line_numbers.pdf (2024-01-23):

1 % _ | _ | _ | _____ _______ _____
2 % | | | | | | | | / ____|__ | __| __ \
3 % | |__| | ___ _ __ ___ | ___| |__ _ __ _____ | __ | | | | | | | | |
4 % | __ |/ _ \| '_ ` _ \ / _ \ '_ \| '__/ _ \ \ /\ / / | | | | | | | | |
5 % | | | | (_) | | | | | | __/ |_) | | | __/\ V V / | |____ | | | | |__| |
6 % |_| |_|\___/|_| |_| |_|\___|_.__/|_| \___| \_/\_/ | \_____| |_| |_____/
7 % (ASCII font Big from https://www.coolgenerator.com/ascii-text-generator
8
9 % Homebrew CTD Data Grapher / Visualizer
10 % Author: Sophie Scopazzi
11 % Author Website: sophiescopazzi.com 12 % Date: OCT 2022
13
14 % always
15 clear all
16 close all
17
18 %% INSTRUCTIONS - HOW TO USE THIS CODE
19 % There are comments throughout code as well
20 % If you want to contact me about this code, use my website 21
22 % 1. Put this script in same folder as datafile.txt
23 % Check name of datafile is the same as in the script
24 % 2. Ensure sensors are in the correct order in the data from the Arduino 25 % script, or none of it will make sense (EC, TDS, sal, etc) in order 26 % 3. Fine correct time values in this plot, record for next step
27 % Want data from downward travel, upward water column is disturbed 28 % 4. Recomment step 3, put the values recorded into DEPLOY DATA PULLING 29 % 5. Plots or subplots as desired. Set xlims and ylims as necessary
30
31 %% 2. DATA INGEST AND CLEANING
32 % datafile from CTD, ensure name is correct, script in same folder as data 33 data = readtable('DATAFILE.TXT');
34
35 % ensure the data is labeled correctly, will depend on Arduino code
36 % get data from data table, BUT it has nans
37 | EC_nans | = | data(:,1); %EC data
38 | TDS_nans | = | data(:,2); %TDS
39 | sal_nans | = | data(:,3); %salinity
40 | mbar_nans | = | data(:,4); %mbar
41 | temp_nans | = | data(:,5); %temp in C
42 | dmeter_nans | = | data(:,6); %depth in meters
43
44 | % take nans out of above data
45 | EC_table | = | rmmissing(EC_nans);
46 | TDS_table | = | rmmissing(TDS_nans);
47 | sal_table | = | rmmissing(sal_nans);
48 | mbar_table | = | rmmissing(mbar_nans);
49 | temp_table | = | rmmissing(temp_nans);
50 | dmeter_table = | rmmissing(dmeter_nans);
51
52 | % convert data from table to array for plotting / manipulation
53 | EC | = | table2array(EC_table);
54 | TDS | = | table2array(TDS_table);

55 | sal | = | table2array(sal_table);
56 | mbar | = | table2array(mbar_table);
57 | temp | = | table2array(temp_table);
58 | dmeter | = | table2array(dmeter_table);
59
60 % convert mbar to feet, incase you want to do that
61 % depth_feet = mbar.*0.033455256555148;
62
63 % convert meters to feet, in case you want to use the Mapping Toolbox 64 % deploy_feet = distdim(dmeter,'meters','feet'); %(needs Mapping Toolbox) 65 dfeet = dmeter.*3.28084; % I didn't want to use Mapping Toolbox
66
67 %% 3. TO FIND CORRECT START / STOP VALUES IN TIME
68 | % FIND TIME VALUES IN THIS PLOT
69 | % look in this plot to find where depth values start and stop
70 | % this is what you will put in below, the (93:135), etc
71 | % uncomment below --- 56-59
72 | % n = length(mbar);
73 | % time = 1:n;
74 | % figure;
75 | % plot(time,mbar);
76
77 %% 4. DEPLOY DATA PULLING
78 | % take out only parts of the data for deployments
79 | % this is the values found 'FIND DEPTH VALUE PLOT'
80 | % if you have more or less than four, change it
81
82 | % ONE
83 | deploy1_EC | = | EC | (93:135,1);
84 | deploy1_TDS | = | TDS | (93:135,1);
85 | deploy1_feet | = | dfeet | (93:135,1);
86 | deploy1_temp | = | temp | (93:135,1);
87 | deploy1_sal | = | sal | (93:135,1);
88
89 | % TWO
90 | deploy2_EC | = | EC | (609:660,1);
91 | deploy2_TDS | = | TDS | (609:660,1);
92 | deploy2_feet | = | dfeet | (609:660,1);
93 | deploy2_temp | = | temp | (609:660,1);
94 | deploy2_sal | = | sal | (609:660,1);
95
96 | % THREE
97 | deploy3_EC | = | EC | (774:799,1);
98 | deploy3_TDS | = | TDS | (774:799,1);
99 | deploy3_feet | = | dfeet | (774:799,1);
100 | deploy3_temp | = | temp | (774:799,1);
101 | deploy3_sal | = | sal | (774:799,1);
102
103 | % FOUR
104 | deploy4_EC | = | EC | (832:979,1);
105 | deploy4_TDS | = | TDS | (832:979,1);
106 | deploy4_feet | = | dfeet | (832:979,1);
107 | deploy4_temp | = | temp | (832:979,1);
108 | deploy4_sal | = | sal | (832:979,1);

109
110 %% 5. GRAPHS
111 % however many you did, make that many subplot graphs
112 % or you can put them on their own plots (not subplot them)
113 % these are the same with the numbers changed, 1-4
114 | figure;
115 | subplot(2,2,1); % subplot since I want four graphs on one figure
116 | plot(deploy1_temp,deploy1_feet,'red');
117 | title('One');
118 | hold
119 | plot(deploy1_sal,deploy1_feet,'blue');
120 | set(gca,'Ydir','reverse'); % to make zero the top of Y axis
121 | ylim([0 40]); | % use the depth you deployed
122 | xlim([14.5 19]) % use the range of your data
123 | legend('temp','salinity')
124 | ylabel('depth (ft)');
125 | xlabel('°C | PSU (ppt)');
126
127 | subplot(2,2,2);
128 | plot(deploy2_temp,deploy2_feet,'red');
129 | title('Two');
130 | hold
131 | plot(deploy2_sal,deploy2_feet,'blue');
132 | set(gca,'Ydir','reverse');
133 | ylim([0 40]); | % use the depth you deployed
134 | xlim([14.5 19]) % use the range of your data
135 | legend('temp','salinity')
136 | ylabel('depth (ft)');
137 | xlabel('°C | PSU (ppt)');
138
139 | subplot(2,2,3);
140 | plot(deploy3_temp,deploy3_feet,'red');
141 | title('Three');
142 | hold
143 | plot(deploy3_sal,deploy3_feet,'blue');
144 | set(gca,'Ydir','reverse');
145 | ylim([0 40]); | % use the depth you deployed
146 | xlim([14.5 19]) % use the range of your data
147 | legend('temp','salinity')
148 | ylabel('depth (ft)');
149 | xlabel('°C | PSU (ppt)');
150
151 | subplot(2,2,4);
152 | plot(deploy4_temp,deploy4_feet,'red');
153 | title('Four');
154 | hold
155 | plot(deploy4_sal,deploy4_feet,'blue');
156 | set(gca,'Ydir','reverse');
157 | ylim([0 40]); | % use the depth you deployed
158 | xlim([14.5 19]) % use the range of your data
159 | legend('temp','salinity')
160 | ylabel('depth (ft)');
161 | xlabel('°C | PSU (ppt)');

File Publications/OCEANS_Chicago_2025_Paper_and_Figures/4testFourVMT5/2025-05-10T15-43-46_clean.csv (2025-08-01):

time | deviceMode | vBat | ec | sal | tds | slowDallasTemp | fastBRTemp | slowBRPres | slowBRTemp | slowBRDepth
2025-05-10T15:54:05 | 1 | 3.94 | 21660.00 | 13.00 | 10399.00 | 999.00 | 9.99 | 1014.40 | 11.12 | 0.01
2025-05-10T15:54:05 | 1 | 3.92 | 21660.00 | 13.00 | 10399.00 | 999.00 | 9.99 | 1015.00 | 11.12 | 0.02
2025-05-10T15:54:05 | 1 | 3.92 | 21660.00 | 13.00 | 10399.00 | 999.00 | 10.01 | 1016.40 | 11.12 | 0.03
2025-05-10T15:54:06 | 1 | 3.94 | 26340.00 | 16.10 | 12644.00 | 999.00 | 10.04 | 1016.40 | 11.11 | 0.03
2025-05-10T15:54:06 | 1 | 3.95 | 26340.00 | 16.10 | 12644.00 | 999.00 | 10.05 | 1016.20 | 11.10 | 0.03
2025-05-10T15:54:06 | 1 | 3.96 | 26340.00 | 16.10 | 12644.00 | 999.00 | 10.07 | 1016.20 | 11.09 | 0.03
2025-05-10T15:54:06 | 1 | 3.95 | 26340.00 | 16.10 | 12644.00 | 999.00 | 10.11 | 1016.80 | 11.09 | 0.04
2025-05-10T15:54:06 | 1 | 3.95 | 26340.00 | 16.10 | 12644.00 | 999.00 | 10.12 | 1017.80 | 11.08 | 0.05
2025-05-10T15:54:07 | 1 | 3.95 | 26530.00 | 16.23 | 12737.00 | 999.00 | 10.14 | 1017.30 | 11.07 | 0.04
2025-05-10T15:54:07 | 1 | 3.94 | 26530.00 | 16.23 | 12737.00 | 999.00 | 10.16 | 1017.30 | 11.07 | 0.04
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

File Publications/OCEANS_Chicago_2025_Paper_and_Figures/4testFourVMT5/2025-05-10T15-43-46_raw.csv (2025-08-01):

time | deviceMode | vBat | ec | sal | tds | slowDallasTemp | fastBRTemp | slowBRPres | slowBRTemp | slowBRDepth
2025-05-10T15:43:49 | 1 | 3.94 | 999.00 | 999.00 | 999.00 | 999.00 | 21.60 | 1018.30 | 22.10 | 0.05
2025-05-10T15:43:51 | 1 | 3.92 | 999.00 | 999.00 | 999.00 | 999.00 | 21.60 | 1018.70 | 22.13 | 0.06
2025-05-10T15:43:51 | 1 | 3.92 | 0.00 | 0.00 | 0.00 | 999.00 | 21.61 | 1018.20 | 22.14 | 0.05
2025-05-10T15:43:52 | 1 | 3.94 | 0.00 | 0.00 | 0.00 | 999.00 | 21.59 | 1018.40 | 22.14 | 0.05
2025-05-10T15:43:52 | 1 | 3.94 | 0.00 | 0.00 | 0.00 | 999.00 | 21.61 | 1018.50 | 22.14 | 0.05
2025-05-10T15:43:52 | 1 | 3.95 | 0.00 | 0.00 | 0.00 | 999.00 | 21.61 | 1018.60 | 22.15 | 0.06
2025-05-10T15:43:52 | 1 | 3.97 | 0.00 | 0.00 | 0.00 | 999.00 | 21.61 | 1018.60 | 22.15 | 0.06
2025-05-10T15:43:52 | 1 | 3.97 | 0.00 | 0.00 | 0.00 | 999.00 | 21.60 | 1018.30 | 22.14 | 0.05
2025-05-10T15:43:53 | 1 | 3.97 | 0.00 | 0.00 | 0.00 | 999.00 | 21.60 | 1018.20 | 22.15 | 0.05
2025-05-10T15:43:53 | 1 | 3.95 | 0.00 | 0.00 | 0.00 | 999.00 | 21.60 | 1018.60 | 22.15 | 0.06
2025-05-10T15:43:53 | 1 | 3.95 | 0.00 | 0.00 | 0.00 | 999.00 | 21.60 | 1018.70 | 22.15 | 0.06
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

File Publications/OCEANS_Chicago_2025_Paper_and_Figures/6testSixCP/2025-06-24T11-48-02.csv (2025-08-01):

time | deviceMode | vBat | ec | sal | tds | slowDallasTemp | fastBRTemp | slowBRPres | slowBRTemp | slowBRDepth
2025-06-24T11:48:06 | 1 | 3.86 | 999.00 | 999.00 | 999.00 | 999.00 | 16.60 | 1042.90 | 16.64 | 0.30
2025-06-24T11:48:08 | 1 | 3.85 | 999.00 | 999.00 | 999.00 | 999.00 | 16.27 | 1045.70 | 16.67 | 0.32
2025-06-24T11:48:08 | 1 | 3.92 | 41210.00 | 26.39 | 19784.00 | 999.00 | 15.99 | 1050.00 | 16.68 | 0.37
2025-06-24T11:48:08 | 1 | 3.88 | 41210.00 | 26.39 | 19784.00 | 999.00 | 15.75 | 1054.60 | 16.68 | 0.41
2025-06-24T11:48:09 | 1 | 3.91 | 41210.00 | 26.39 | 19784.00 | 999.00 | 15.53 | 1058.10 | 16.67 | 0.45
2025-06-24T11:48:09 | 1 | 3.91 | 42630.00 | 27.40 | 20463.00 | 999.00 | 15.31 | 1060.50 | 16.65 | 0.47
2025-06-24T11:48:09 | 1 | 3.89 | 42630.00 | 27.40 | 20463.00 | 999.00 | 15.10 | 1065.40 | 16.64 | 0.52
2025-06-24T11:48:09 | 1 | 3.90 | 42630.00 | 27.40 | 20463.00 | 999.00 | 14.92 | 1066.50 | 16.62 | 0.53
2025-06-24T11:48:09 | 1 | 3.89 | 42630.00 | 27.40 | 20463.00 | 999.00 | 14.75 | 1065.00 | 16.59 | 0.52
2025-06-24T11:48:10 | 1 | 3.90 | 42630.00 | 27.40 | 20463.00 | 999.00 | 14.57 | 1064.40 | 16.56 | 0.51
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

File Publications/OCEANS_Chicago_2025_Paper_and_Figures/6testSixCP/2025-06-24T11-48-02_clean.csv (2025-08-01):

time | deviceMode | vBat | ec | sal | tds | slowDallasTemp | fastBRTemp | slowBRPres | slowBRTemp | slowBRDepth
2025-06-24T11:48:36 | 1 | 3.89 | 36970.00 | 23.39 | 17746.00 | 999.00 | 14.29 | 1021.50 | 14.55 | 0.08
2025-06-24T11:48:37 | 1 | 3.88 | 36970.00 | 23.39 | 17746.00 | 999.00 | 14.29 | 1022.20 | 14.56 | 0.09
2025-06-24T11:48:37 | 1 | 3.91 | 36970.00 | 23.39 | 17746.00 | 999.00 | 14.27 | 1022.90 | 14.56 | 0.10
2025-06-24T11:48:37 | 1 | 3.90 | 36970.00 | 23.39 | 17746.00 | 999.00 | 14.23 | 1023.90 | 14.56 | 0.11
2025-06-24T11:48:37 | 1 | 3.88 | 36970.00 | 23.39 | 17746.00 | 999.00 | 14.20 | 1025.40 | 14.56 | 0.12
2025-06-24T11:48:37 | 1 | 3.91 | 43620.00 | 28.11 | 20939.00 | 999.00 | 14.15 | 1025.50 | 14.57 | 0.12
2025-06-24T11:48:38 | 1 | 3.90 | 43620.00 | 28.11 | 20939.00 | 999.00 | 14.12 | 1025.90 | 14.57 | 0.13
2025-06-24T11:48:38 | 1 | 3.90 | 43620.00 | 28.11 | 20939.00 | 999.00 | 14.08 | 1026.30 | 14.57 | 0.13
2025-06-24T11:48:38 | 1 | 3.89 | 43620.00 | 28.11 | 20939.00 | 999.00 | 14.05 | 1027.90 | 14.57 | 0.15
2025-06-24T11:48:38 | 1 | 3.88 | 43620.00 | 28.11 | 20939.00 | 999.00 | 14.02 | 1029.10 | 14.57 | 0.16
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

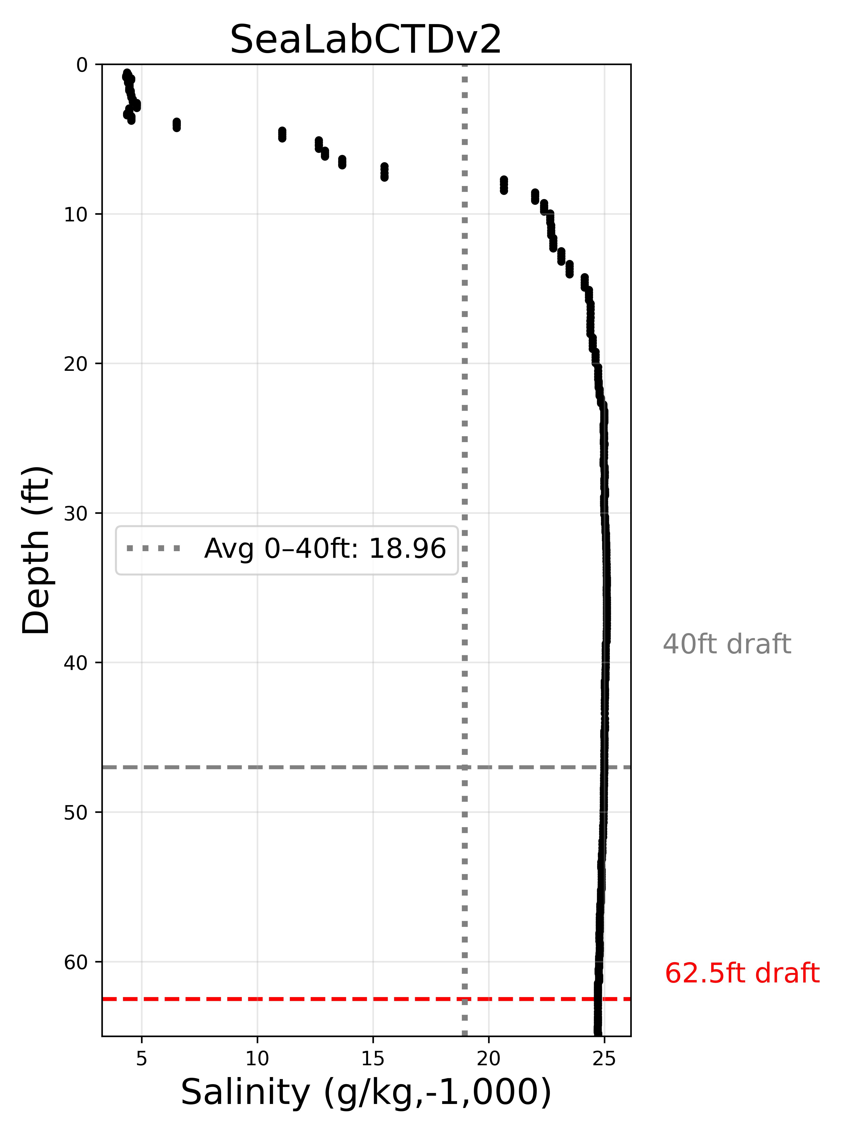
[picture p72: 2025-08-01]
Publications/OCEANS_Chicago_2025_Paper_and_Figures/7testSevenVMT5/testSixCP_profile_salt_AKL_plot.jpg

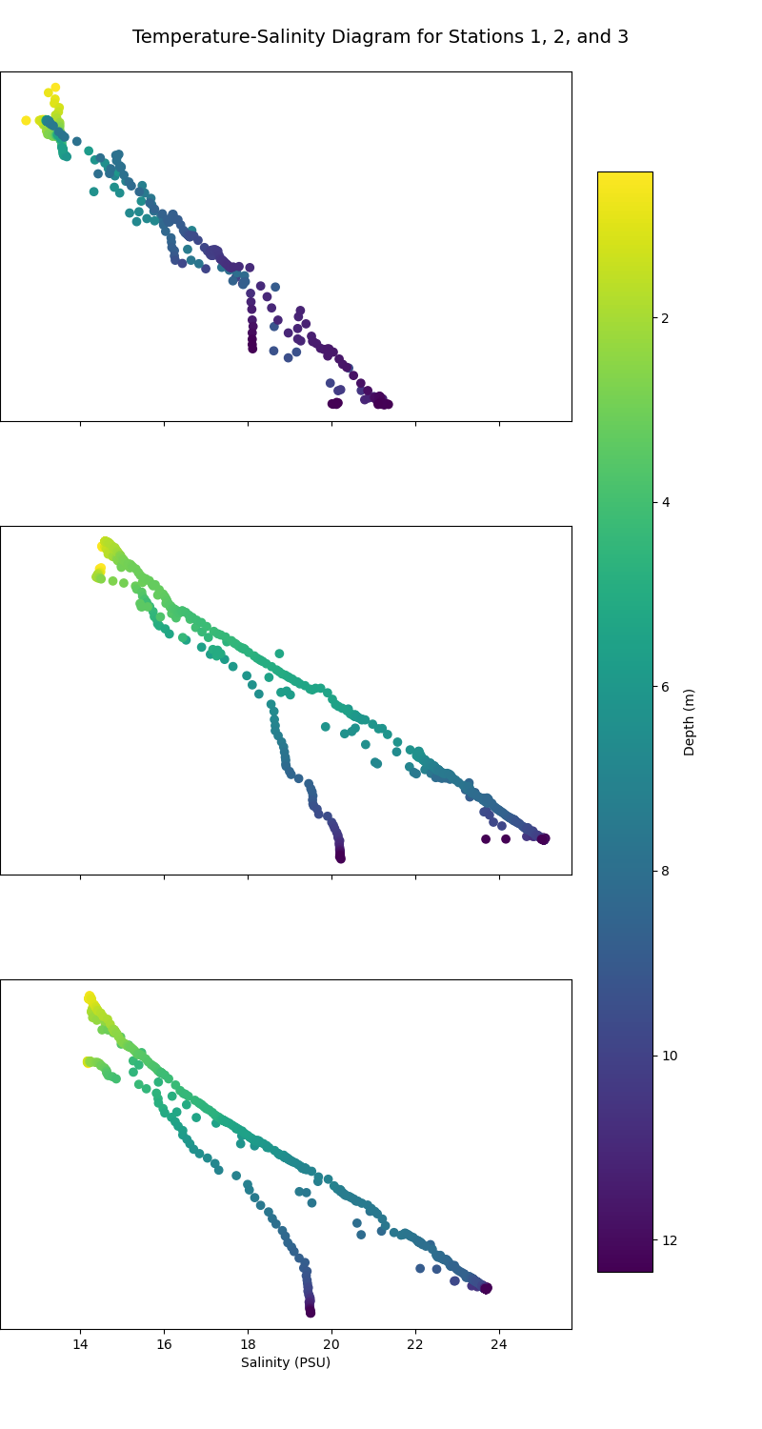
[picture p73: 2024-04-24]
z_v1/SeaLabCTD_v1/a_test_data/2024.4.17 RV Rutgers/TS_comparison.png

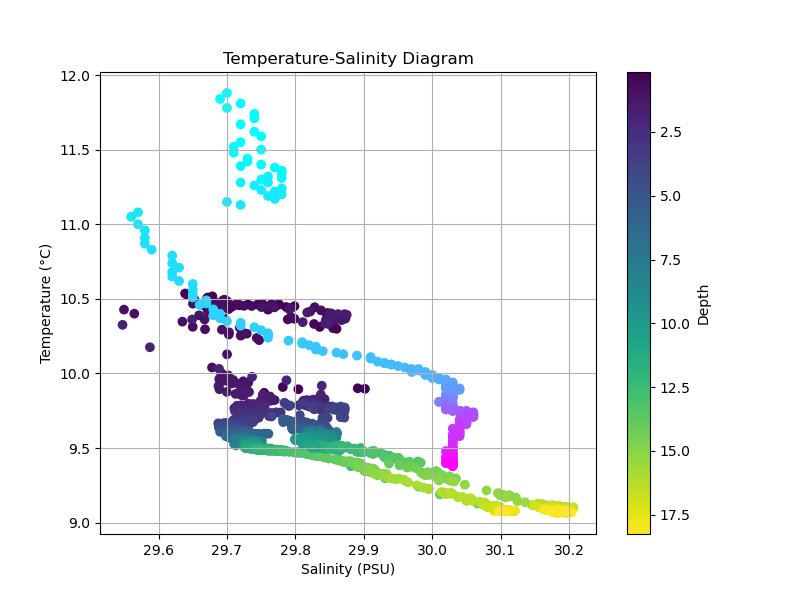
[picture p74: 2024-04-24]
z_v1/SeaLabCTD_v1/a_test_data/2024.4.22 RV Rutgers/ts_plot.png

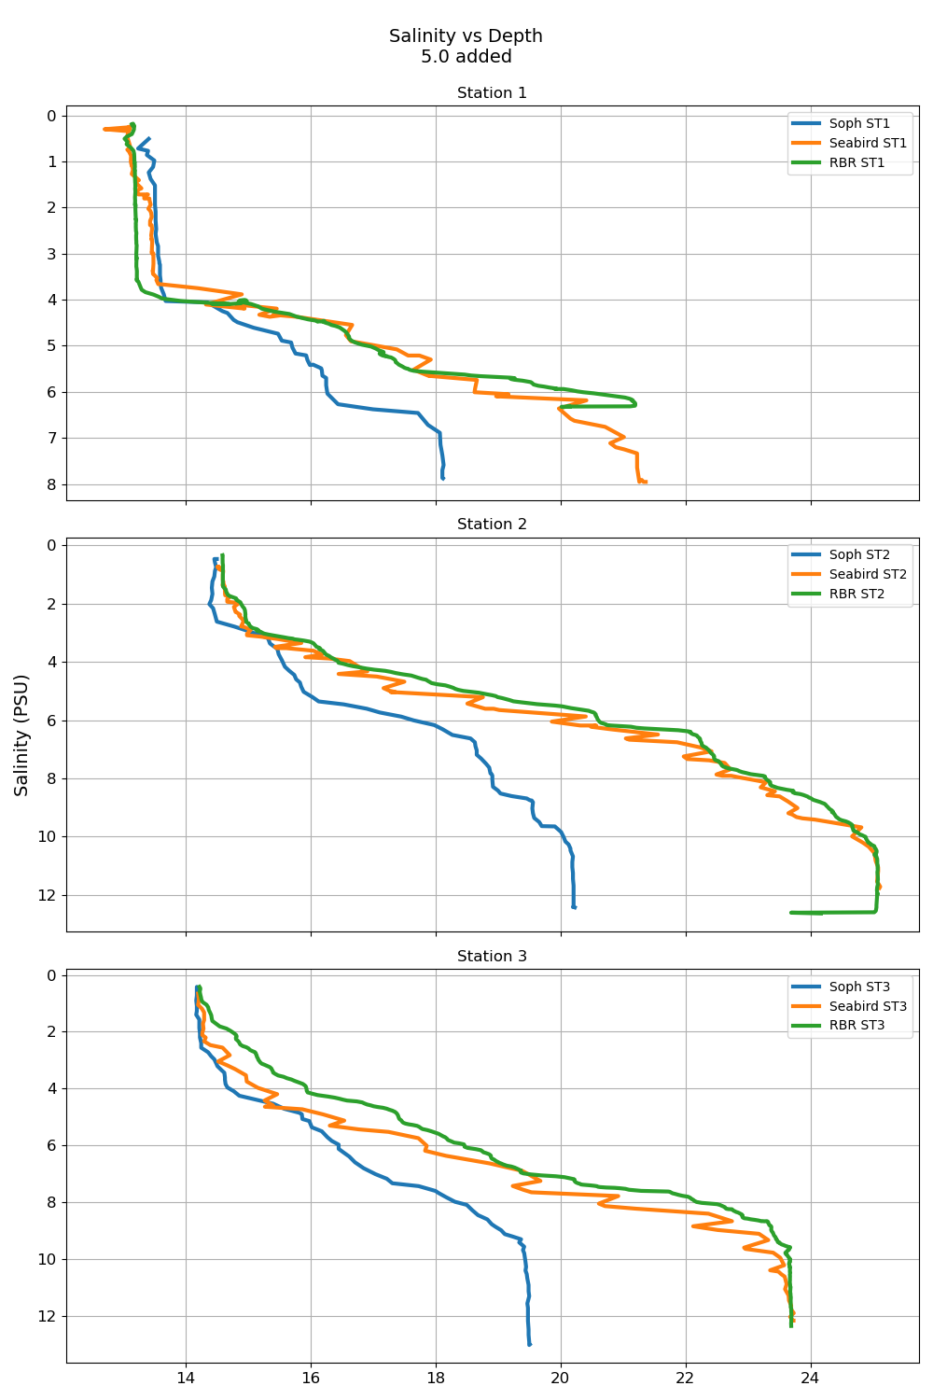
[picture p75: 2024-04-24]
z_v1/SeaLabCTD_v1/a_test_data/2024.4.17 RV Rutgers/compare_sal.png

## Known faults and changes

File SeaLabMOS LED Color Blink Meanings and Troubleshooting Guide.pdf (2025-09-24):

On startup, the sytem with flash the onboard LED 5 times to denote the deviceMode

Device Mode | Meaning | Color
0 | Fast sampling every loop | Bright Green, LED always on
1 | 1-minute mode | Orange
2 | 10-minute mode | Yellow
3 | Charge mode (LED always on) | Purple
4 | Bottom Pressure Recorder | Cyan
5 | Pressure Only Profile | White
Other / Unknown | Unknown mode (will not sample) | Red

Immeditely afterwards, it will show the battery voltage with the LED using the following scale If you see both colors (red and purple) it means the voltage is floating between the two

Battery Voltage (V) | Meaning | Color
>=4.0 | Full | Green
3.8–3.6 | Mostly full | Cyan
3.6–3.5 | Medium | Yellow
3.5–3.35 | Low | Purple
3.35–3.2 | Critical (no blink) | Red
<3.2 | Dangerously low *FLASHES* | Red

For any questions or issues, please call/text/email Sophie Scopazzi Phone: (text first please unless time sensitive) 707-520-4460
Email: aspectwave@pm.me
Website: https://www.aspectwave.io/
Website: https://www.sophiescopazzi.com/projects/sealabmos GitHub: https://github.com/sscopazzi/SeaLabMOS

If troubleshooting, it will output to serial via the USB-C at 115200 baud

### SeaLabMOS LED Color/Blink Meanings and Troubleshooting Guide

(v4 2025.9.22)

You will know the SeaLabMOS system is ready to deploy once it has flashed the deviceMode and shown the battery voltage, then nothing further. If the sensor(s) initilaize properly and the microSD card is detected and can be written to the LED is not utilized further to save power.

Continual red flashes can happen after the before two light patterns when the microSD card and/or sensor(s) is/are not detected

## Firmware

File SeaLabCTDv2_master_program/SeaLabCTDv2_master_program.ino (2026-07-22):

// RP2040 NEEDS THIS TO BE IN ARDUINO IDE FOR BOARDS
// https://github.com/earlephilhower/arduino-pico/releases/download/global/package_rp2040_index.json

// Coming features...
// 1. GNSS sensor
// 2. Salinity temp comp RT command, see how well this actually changes anything????
// 3. Auto-select sensors based on system type (CTD, BPR, temp logger, etc)??
// 4. Wired system version, using ethernet and PoE
// 5. RF/BT data offload for fully sealed system with subconn connector for charging?
// 6. Pair with open source niskin bottles and make a rosette 
// 7. Open source fluorometer

int deviceMode = 5;
// 0 = fast as possible
// 1 uses WAIT_TIME_ONE
// 2 uses WAIT_TIME_TWO
// 3 is charge mode 
// 4 is BPR (samples at 4-5Hz first 20min of every hr)
// 5 is continuous pressure recording 
// 6 is surface float (or location recorder - it doesn't have to float) GPS-only at 10Hz (no RTC, GPS timestamp, Serial1) for ocean currents / paths

bool serialDisplay  = true;  // Set to false to disable all Serial prints after the setup 
bool displayBool    = false; // Adafruit Feather OLED Display
int timeZone        = -8;    // time zone of commputer time, as program pulls time from computer to set RTC, but must convert

// ###### SENSORS USED BY SYSTEM ######
bool salinityBool = false;  // Atlas Scientific Salinity Sensor
bool ecBool       = false;  // is value enabled on EZO circuit to send?
bool sBool        = false;  // is value enabled on EZO circuit to send?
bool tdsBool      = false;  // is value enabled on EZO circuit to send?
bool sgBool       = false;  // is value enabled on EZO circuit to send?

// ###### TEMPERATURE ######
bool dallasTempBool = false;  // Dallas Temperature sensor
bool thermTempBool  = false;  // Adafruit Thermistor
bool pt100Bool      = false;  // Adafruit PT100
bool brFastTempBool = false;  // Blue Robotics Fast Temperature, powered permanently via Qwiic/STEMMA QT 3.3V

// ###### PRESSURE ######
bool pressDFBool  = false;  // DF Robot analog pressure sensor
bool bar02Bool    = false;  // Blue Robotics Bar02
bool bar30Bool    = true;  // Blue Robotics Bar30, all other systems use this one, except BPR
bool bar100Bool   = false;  // Blue Robotics Bar100, currently STEEL only

// ###### UTILITY ######
bool beaconBool = false;  // Surface float LED beacon

// ###### OTHER SENSORS ######
bool lightBool = false;  // Adafruit AS7262 6-channel Visible Light Sensor, only this on the TWOIN
bool gpsBool   = false;  // Adafruit GPS FeatherWing (Serial1)
                         // Do NOT enable gpsBool and salinityBool simultaneously (both use Serial1)
                         // Mode 6 automatically uses gpsSetup10Hz() — set gpsBool = true and deviceMode = 6

#define WAIT_TIME_ONE 1   // 1 min (other: 5 min, 20 min, 30 min, etc.)
#define WAIT_TIME_TWO 10  // 10 min (other: 1 hr, 12 hr, 24 hr, etc.)
#define WAIT_TIME_BPR 20  // First 20 min of the hour (for Bottom Pressure Recorder)

// GPIO PIN SETTINGS ######
#define RTC_INTERRUPT_PIN   25  // RTC interrupt pin
#define BEACON_PIN          11  // enable 3.3V->12V board to power LED surface beacon
#define SALINITY_ENABLE_PIN 4   // enable pin for salinity board

// ANALOG PINS
#define THERMISTOR_PIN  A3  // Analog pin used for thermistor
#define BATTV_PIN       A2  // Analog pin used for battery voltage monitoring

// OTHER VALUES
#define SYSTEM_BAUD   115200 // Serial with computer
#define SALINITY_BAUD 9600   // baud rate of EZO circuit, default is 9600
#define WATER_DENSITY 1029   // 1029 is default seawater for Blue Robotics sensors

// SEALABCTD UTILILITY HEADER FILES
#include "globals.h"         // self made file
#include "systemNames.h"     // contains all system names 
#include "display.h"         // Adafruit_SH110x and Adafruit_GFX
#include "ledDisplay.h"      // Functions for flashing the NeoPixel and orange beacon for surface assets
#include "battMonitoring.h"  // Battery monitoring functions

// SEALABCTD SENSOR HEADER FILES
#include "blueRoboticsPressure.h"  // Blue Robotics' pressure sensors
#include "blueRoboticsFastTemp.h"  // Blue Robotics' Fast Temperature sensor
#include "salinAtlas.h"            // Atlas Scientific Conductivity Sensor
#include "dallasTemp.h"            // DS18B20 "dallas" temperature sensors, OneWire library by Jim Studt, Tom Pollard
#include "therm.h"                 // Adafruit 10kΩ NTC thermistor
#include "pt100.h"                 // Adafruit PT100
#include "pressDF.h"               // DF Robot Analog Pressure Sensor (required 3.3V->5V buck)
#include "light.h"                 // 6-channel light sensor
#include "gps.h"                   // Adafruit GPS FeatherWing
// ############################################################################################################

void setup() {
  // MUST CHANGE CLOCK SPEED BEFORE DOING ANYTHING ELSE
  // Needs more research and testing as sometimes it breaks the timing of certain sensors
  // If having issues sampling with sensors using master code but single sensor code works, use default clock speed 133MHz
  switch (deviceMode) {
    case 0:                             // fast sampling
      set_sys_clock_khz(133000, true);  // safer default
      // set_sys_clock_khz(200000, true); // overclocking, untested
      delay(5);
      yield();
      break;
    case 1:  // WAIT TIME 1
    case 2:  // WAIT TIME 2
    case 4:  // BPR
    case 5:  // PRESS_ONLY always recording pressure
    case 6:  // GPS surface float — no heavy processing, keep clock low
      set_sys_clock_khz(50000, true);
      delay(5);
      yield();
      break;
    default:
      set_sys_clock_khz(133000, true);
      delay(5);
      yield();
      break;
  }

  if (displayBool) {            // Start display first to then show system boot process
    display.clearDisplay();     // Make sure nothing is in the buffer
    display.begin(0x3C, true);  // Address 0x3C default, specify address for use later shutting of the display
    display.setRotation(1);
    display.setTextSize(1);
    display.setTextColor(SH110X_WHITE);
    display.display();
    delay(2500);  // display Adafruit splashscreen cuz we love Adafruit Industries
    display.clearDisplay();
    display.setCursor(0, 0);
    display.println("SeaLabCTD Start <3");
    display.display();
  }

  if (salinityBool) { salinSetup(); }  // SETUP SALINITY
  if (salinityBool && displayBool) {
    display.println("Salinity init");
    display.display();
  }

  if (serialDisplay) {
    Serial.begin(SYSTEM_BAUD);
    // while (!Serial) { delay(10); }  // THIS MAKES IT HANG SO NFG
    delay(5000);
    // readBatteryVoltage();
    // Serial.print("SYSTEM STARTUP --> voltage is"); Serial.print(battV); Serial.println(" volts");
    Serial.print("deviceMode = "); Serial.println(deviceMode);  // ground truth
  }

  analogReadResolution(12);  // specify in code for proper battV and thermistor reference

  // if (serialDisplay) Serial.println("Wire init...");
  Wire.begin();
  Wire.setClock(100000);  // force standard 100kHz I2C, don't let it float at 50MHz-scaled default
  delay(100);

  if (serialDisplay) {
  Serial.println("Scanning Wire bus...");
  for (byte addr = 1; addr < 127; addr++) {
    Wire.beginTransmission(addr);
    byte err = Wire.endTransmission();
    if (err == 0) {
      Serial.print("Found device at 0x");
      Serial.println(addr, HEX);
    }
  }
  Serial.println("Scan done");
  }

  pinMode(THERMISTOR_PIN, INPUT);
  setupBatteryMonitoring((deviceMode == 3) ? CHARGE_MODE : SAMPLE_MODE);  // Battery LED policy
  blinkDeviceModeLED(deviceMode);

  if (!displayBool && (deviceMode == 1 || deviceMode == 2 || deviceMode == 4 || deviceMode == 5)) {
    uint32_t start = millis();
    while (millis() - start <= 7000) {  // keep LED on 7 seconds
      readBatteryVoltage();
      updateBatteryLED(battV);
      yield();
    }
    if (serialDisplay) Serial.println("Disabling LED after 7 sec");
    pixel.setPixelColor(0, 0);
    pixel.show();
  }

  if (dallasTempBool) { setupDallasTemp(); }
  if (dallasTempBool && displayBool) {
    display.println("dallasTemp init");
    display.display();
  }

  if (lightBool) { setupLight(); }
  if (lightBool && displayBool) {
    display.println("6-ch light init");
    display.display();
  }

  if (gpsBool) {
    if (deviceMode == 6) {
      gpsSetup10Hz();  // 57600 baud, RMC only, 10 Hz — no RTC needed
    } else {
      gpsSetup();      // 9600 baud, RMC+GGA, 1 Hz
    }
    if (displayBool) {
      display.println(deviceMode == 6 ? "GPS 10Hz init" : "GPS 1Hz init");
      display.display();
    }
  }

  if (bar02Bool || bar30Bool || bar100Bool) {
    brPressureSetup();
    if (displayBool) {
      display.println("brPressure init");
      display.display();
    }
  }

  // delay(200);

  // thermTemp does not have a setup function (fully analog sensor)
  if (thermTempBool && displayBool) {
    display.println("thermTemp init");
    display.display();
  }

  if (pt100Bool) { pt100Setup(); }
  if (pt100Bool && displayBool) {
    display.println("PT100 init");
    display.display();
  }

  delay(200);

  // Mode 6 (GPS surface float) has no RTC — skip entirely, GPS provides the timestamp
  if (deviceMode != 6) {
    if (!rtc.begin()) {
      if (serialDisplay) Serial.println("Could not find RTC");
      Serial.flush();
      while (1) {
        redFlash();  // without RTC we do not continue so flash Neopixel red
      }
    }

    rtc.writeSqwPinMode(DS3231_OFF);  // disable square wave because we want to use as interrupt

    if (rtc.lostPower()) {
      setRtcCompileTimeUTC();  // uses the timeZone variable already defined
    }

    // When time needs to be re-set on a previously configured device, the
    // following line sets the RTC to the date & time this sketch was compiled
    // rtc.adjust(DateTime(F(__DATE__), F(__TIME__))); // time of computer, no UTC
    // setRtcCompileTimeUTC();

    rtc.clearAlarm(1);
    delay(2);  // tiny debounce delay for some DS3231 boards, not 100% sure if needed
    rtc.clearAlarm(2);
    delay(2);  // tiny debounce delay for some DS3231 boards, not 100% sure if needed

    pinMode(RTC_INTERRUPT_PIN, INPUT_PULLUP);
    attachInterrupt(digitalPinToInterrupt(RTC_INTERRUPT_PIN), rtcWakeISR, FALLING);

    if (displayBool) {
      display.println("RTC init");
      display.display();
    }
    delay(200);
  } else {
    if (serialDisplay) Serial.println("Mode 6: RTC skipped, GPS provides timestamp");
  }

  if (brFastTempBool) {
  if (serialDisplay) Serial.println("brFastTemp setup...");
    brFastTempSetup();
      if (displayBool) {
        display.println("brFastTemp init");
        display.display();
      }
  }

  // Try to initialize SD card
  if (!SD.begin(config)) {
    if (serialDisplay) Serial.println("SD card initialization FAILED!");
    if (displayBool) {
      display.clearDisplay();
      display.setCursor(0, 0);
      display.println("SD init FAILED");
      display.println("Check wiring/config");
      display.display();
      delay(3000);
    }
    if (serialDisplay) Serial.println("No SD card logging possible. Halting...");
      while(true){
        redFlash();
      }
    } else {
      if (serialDisplay) Serial.println("SD card initialized OK");
      if (displayBool) {
        display.println("SD init OK");
        display.display();
      }
  }

  pinMode(BUTTON_A, INPUT_PULLUP);  // not used yet
  pinMode(BUTTON_B, INPUT_PULLUP);  // not used yet
  pinMode(BUTTON_C, INPUT_PULLUP);  // not used yet

  // Set the first alarm based on mode to start sampling on even numbers
  // Mode 6 skips this entirely — no RTC, no alarms needed
  if (deviceMode != 6) {
    currentTime = rtc.now();

    if (deviceMode == 4) { bprSampling = (currentTime.minute() < 20); }

    if (deviceMode == 1) { nextSample = getNextAlarm(currentTime, WAIT_TIME_ONE);

      if (serialDisplay) { Serial.println("Initial Alarm One set");  }
      if (displayBool)   { alarmDisplay(WAIT_TIME_ONE, "Alarm One"); }
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

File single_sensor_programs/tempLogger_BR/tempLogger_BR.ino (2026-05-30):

// ============================================================
// RTC_FastTemp_Test.ino
// DS3231 RTC  on Wire  — GPIO 2 (SDA)  / GPIO 3 (SCL)   [I2C1, default]
// TSYS01 fast temp on Wire1 — GPIO 12 (SDA) / GPIO 13 (SCL) [I2C0]
//   Wire your TSYS01 SDA -> D10, SCL -> D11 on the Feather header
//
// TSYS01 powered from GPIO 5, fully off between samples.
// RTC alarm wakes from sleep every WAIT_MINUTES (mode 1 style).
// ============================================================

#include <Arduino.h>
#include <Wire.h>
#include <RTClib.h>   // Adafruit RTClib
#include "TSYS01.h"   // Blue Robotics TSYS01

#include "pico/stdlib.h"
#include "hardware/sync.h"  // __wfi()

// ---------------------------------------------------------------
// USER CONFIG
// ---------------------------------------------------------------
#define BR_SENSOR_POWER_PIN   5     // GPIO powering TSYS01 VCC
#define RTC_INTERRUPT_PIN     25    // DS3231 SQW/INT pin
#define WAIT_MINUTES          1     // alarm interval
#define SYSTEM_BAUD           115200
#define TIME_ZONE             -7    // local offset for compile-time UTC set

// Wire1 pins — D10 = GPIO10 (SDA1), D11 = GPIO11 (SCL1)
#define WIRE1_SDA_PIN  10
#define WIRE1_SCL_PIN  11
// ---------------------------------------------------------------

RTC_DS3231 rtc;
TSYS01     fastTempSensor(&Wire1);  // TSYS01 on Wire1

volatile bool rtcAlarmFired = false;
void rtcWakeISR() { rtcAlarmFired = true; }

// ---------------------------------------------------------------
// Next alarm aligned to WAIT_MINUTES boundary
// ---------------------------------------------------------------
DateTime getNextAlarm(DateTime now, uint8_t waitMinutes) {
  uint8_t  nextMinute = ((now.minute() / waitMinutes) + 1) * waitMinutes;
  uint8_t  nextHour   = now.hour();
  uint8_t  nextDay    = now.day();
  uint8_t  nextMonth  = now.month();
  uint16_t nextYear   = now.year();

  if (nextMinute >= 60) {
    nextMinute %= 60;
    nextHour++;
    if (nextHour >= 24) { nextHour = 0; nextDay++; }
  }
  return DateTime(nextYear, nextMonth, nextDay, nextHour, nextMinute, 0);
}
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

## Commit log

2024-01-23 initial commit of files
    [CTD2020 SMOOTHER SIDES.skp, CTD2020 Smoother Sides STL.stl, CTD2020 Smoother Sides.stl, CTD2020 end cap.skp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]
2024-04-20 added basic list of sensors
2024-04-20 calibrated salinity 2024.4.20
2024-04-20 removed print to serial monitor, less delay betwen loops
2024-04-24 init new test
    [Castaway_11D101493_20240422_171552_downup.csv, Castaway_11D101493_20240422_171552_processed.csv, Castaway_11D101493_20240422_171552_raw.csv]
2025-08-01 initial upload for MTS paper, needs more work
    [2025-04-29T14-31-17.csv, 2025-04-29T14-31-17_first_clean.csv, 2025-04-29T14-31-17_first_down.csv, 2025-04-29T14-31-17_first_up.csv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]
2025-09-03 light sensor added
2025-09-06 red flash at 3.4V now
2025-09-20 added list of sensors
2025-09-21 initial wire diagram
    [SeaLabMOS.kicad_sch]
2025-09-21 added GNSS
    [SeaLabMOS.kicad_sch]
2025-09-22 changed LED colors, flashes when critical with redFlash()
2025-09-22 v1 of LED color/blink explanation sheet
    [2025.9.21v1 SeaLabMOS LED Color Blink Meanings and Troubleshooting Guide.xlsx]
2025-09-22 v1 PDF LED blink/color meaning
    [2025.9.21v1 SeaLabMOS LED Color Blink Meanings and Troubleshooting Guide.xlsx]
2025-09-22 swapped deviceMode 5 (said red, correct white)
2025-10-07 added image, reorganized sensors
2025-10-14 initial 2in parts
    [2in_datalogger.SLDPRT, 2in_datalogger.STL, 2in_sensor_drill_area.SLDPRT, 2in_sensor_drill_area.STL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]
2025-11-13 preface, build steps
    [SeaLabMOS_Two-Week_Intensive.xlsx]
2026-05-28 salinity sensor only .ino
2026-05-30 try power switching fast temp sensor, no work...
2026-06-14 added pressure only schedule 80 pipe
